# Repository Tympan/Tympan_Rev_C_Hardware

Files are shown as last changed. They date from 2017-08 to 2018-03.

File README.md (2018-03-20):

# Tympan_Rev_C_Hardware
Repository for the board files for Tympan Rev C

These design files were made with [KiCAD](http://kicad-pcb.org/) PCB capture software. The custom component files for parts used in this design are located in the repo as well. Everything should render correctly in the Schematic and the PCB. If not, you may need to adjust the library paths. 

This work is based on work done by Creare and their team in Spring of 2017. Modifications have been made to their Rev A hardware design to overcome bugs and improve the design. 

## Works with Teensy 3.6
The [Teensy 3.6](https://www.pjrc.com/store/teensy36.html) from PJRC is the 'brain' that drives our audio board. In order to make the Tympan and the Teensy live happily together, you will need to modify the Teensy board as shown.

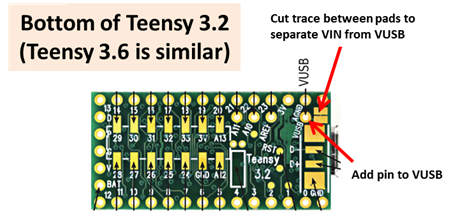
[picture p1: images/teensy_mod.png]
Teensy_Mod


The change allows us to use the VUSB (5V) to charge the LiIon battery with circuitry on the Tympan. That's it! Follow the [getting started guide](https://www.pjrc.com/teensy/first_use.html) for the Teensy, and then you will be up and running with our [Tympan Library](https://github.com/Tympan/Tympan_Library) for Arduino!

## Enclosure
The Tympan Case is 3D printed, and the design files can be found [here](https://github.com/Tympan/Tympan_Rev_C_Hardware/tree/master/Enclosure) There is also a Bill of Materials that will list the screws and threaded inserts that we used. 

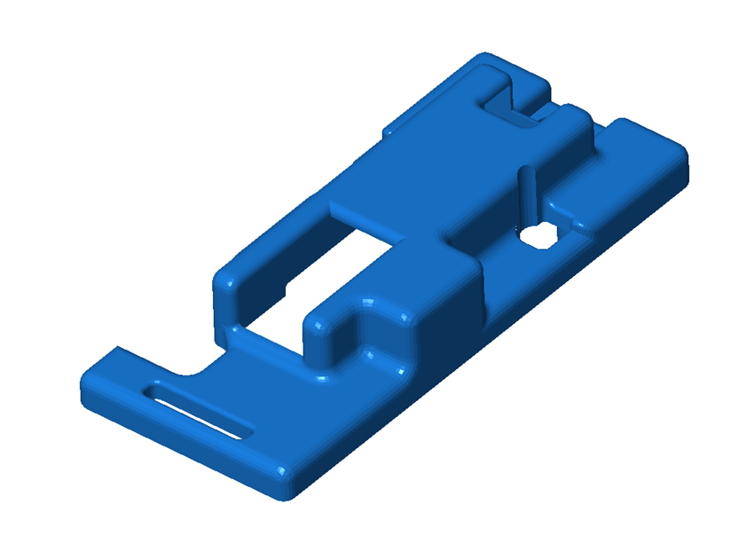
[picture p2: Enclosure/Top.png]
Tympan Case Top

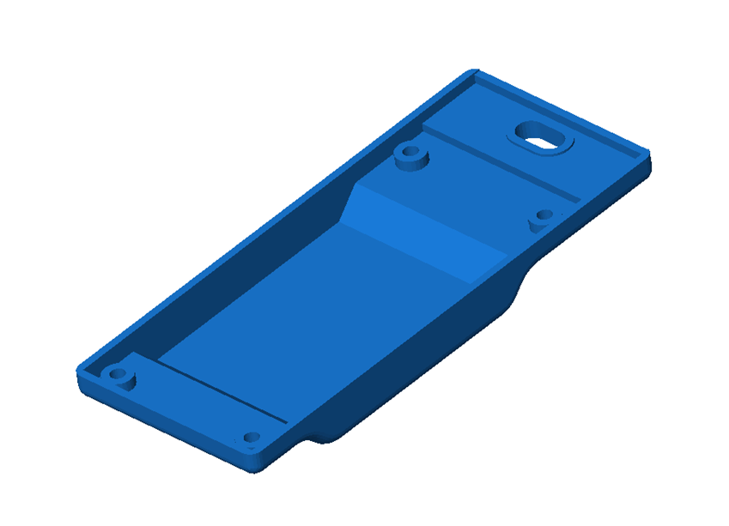
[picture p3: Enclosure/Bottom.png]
Tympan Case Bottom


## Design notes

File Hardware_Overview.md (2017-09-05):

# Tympan Hardware Overview
## Tympan Audio Board RevC

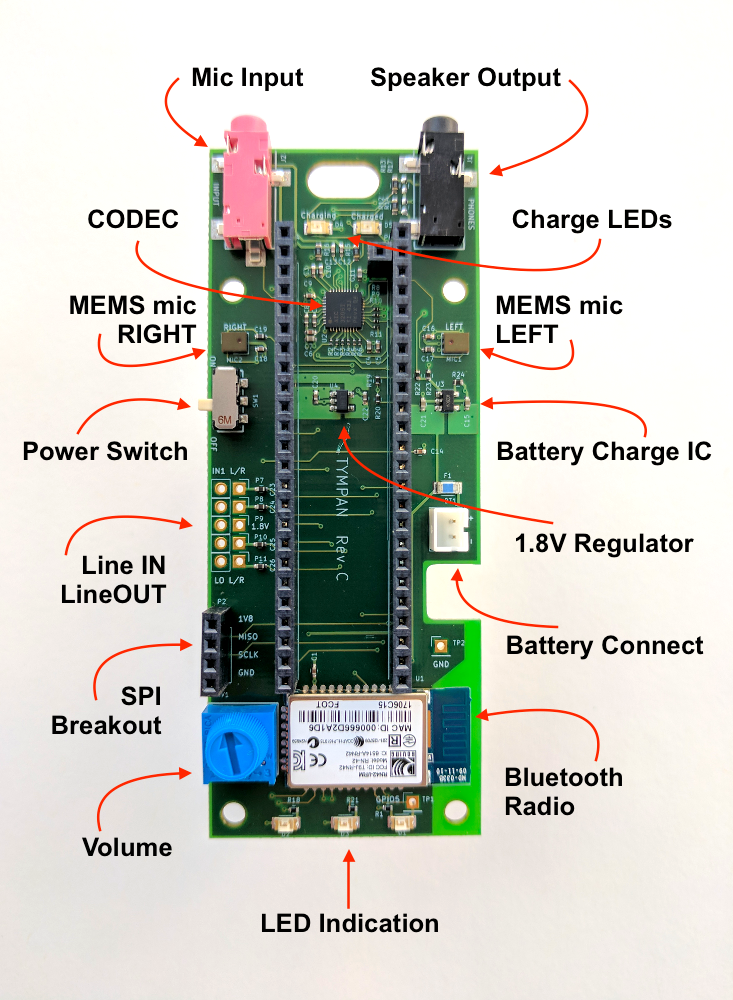
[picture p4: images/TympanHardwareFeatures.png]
Tympan Under The Hood


## Tympan assembled with Teensy 3.6

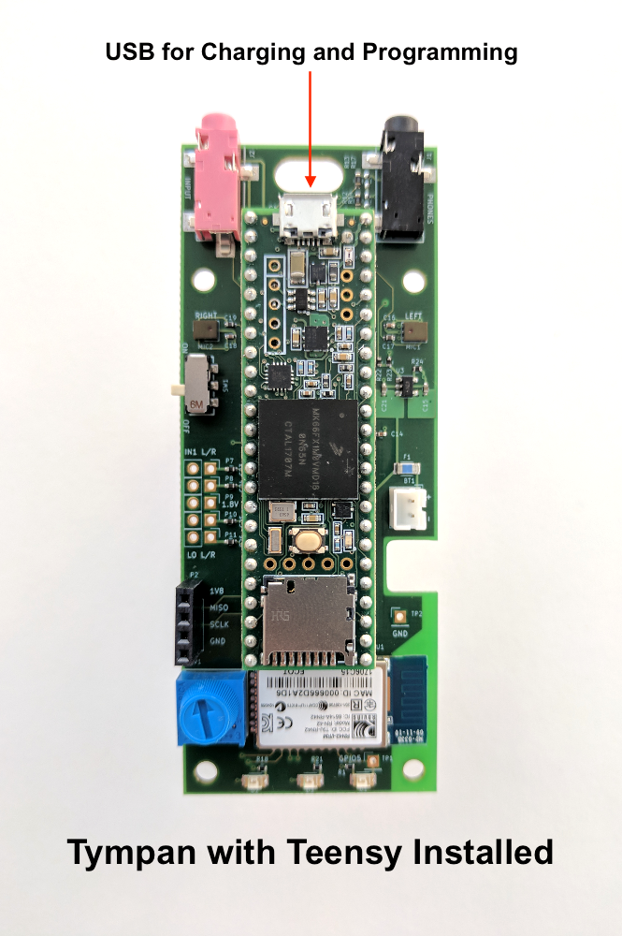
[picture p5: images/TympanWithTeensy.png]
Naked Tympan


## Hardware Modifications 

The Tympan RevC is Open Source Hardware, and that means that you can hack it or mod it and we will be here to help! There are a couple of possible mods that are baked into the hardware.

### Mic Input Jack

The MIC input jack is the pink one. The way that it has been wired to the CODEC causes the following things to happen when you plug into it:

* Mono consumer MIC (one element), you get mono into Tympan
* Stereo consumer MIC (two elements), you get mono (just the left mic is active)
* Hearing-Aid MIC (one element), you get mono into Tympan
* Stereo line-in, you get stereo into Tympan

It is possible to modify the hardware to change the MIC Input Jack behavior. If you add a 2.2K Resistor to the unpopulated R16 position, you will change the MIC input behavior to:

* Mono consumer mic (one element), you get mono into Tympan
* Stereo consumer mic (two elements), you get stereo
* Hearing-Aid Mic (one element), you get nothing
* Stereo line-in, you get nothing

### Line IN / OUT

We have broken out the `IN1` RIGHT and LEFT channels for your use. Also, the CODEC has a Line OUT channel which is also broken out. The pins available are laid out in standard 0.1" pitch, and can be soldered to as you see fit. We also breakout the 1.8V power line between them for your use a a bias voltage. You're welcome ;)

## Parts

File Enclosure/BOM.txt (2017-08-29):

Bill of Materials:

1	Tympan Rev C
1	Teensy 3.6 with 0.1" header pins soldered to each row
		- Modify Teensy by cutting trace to seperate VIN from VUSB
		- Modify Teensy by adding single 0.1" pin to VUSB through hole
1	Enclosure Top (10000200_r2)
1	Enclosure Bottom (10000167 rev3)
4	Stainless Screw-to-Expand Inserts for Plastics (McMaster-Carr P/N: 92394A112)
4	5/16" Stainless Phillips Rounded Head Screws (McMaster-Carr P/N: 91772A107)
1	Lithium Ion Polymer Battery, 3.7v 500mAh (Adafruit: Product ID 1578)

Also, add Kapton tape to bottom of Tympan PCB to electrically isolate it from the battery.

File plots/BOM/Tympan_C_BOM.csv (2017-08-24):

Id | Designator | Package | Quantity | Designation | Manufacturer | Part Number
1 | BT1 | JST_PH_B2B-PH-K_02x2.00mm_Straight | 1 | LiPo | JST Sales | B2B-PH-K-S(LF)(SN)
2 | D2,D4 | C_1206 | 2 | LED, Red | Lite-On | LTST-C150EKT
3 | D1 | C_1206 | 1 | LED, Blue | Lite-On | LTST-C150TBKT
4 | D3 | C_1206 | 1 | LED, Amber | Lite-On | LTST-C150AKT
5 | D5 | C_1206 | 1 | LED, Green | Lite-On | LTST-C150GKT
6 | F1 | C_1206 | 1 | FUSE | Bell Fuse | C1Q 1
7 | MIC2,MIC1 | SPH1642HT5H | 2 | SPH1642HT5H-1 | Knowles | SPH1642HT5H-1
8 | TP1,TP2 | DNP | 2 | DNP | DNP | DNP
9 | P5 | Pin_Header_Straight_1x01_Pitch2.54mm | 3 | CONN_01X01 | Samtec | SSW-101-01-G-S
10 | P2 | Pin_Header_Straight_1x04_Pitch2.54mm | 1 | CONN_01X04 | Samtec | SSW-104-01-G-S
11 | P4,P6 | Pin_Header_Straight_1x24_Pitch2.54mm | 2 | CONN_01X24 | Samtec | SSW-124-01-G-S
12 | P7,P8,P9,P10,P11 | DNP | 5 | DNP | DNP | DNP
13 | R12,R13 | C_0603 | 2 | 0R | Vishay Dale | CRCW06030000Z0EA
14 | R14,R16,R17 | DNP | 3 | DNP | DNP | DNP
15 | RV1 | Bourns_3386F | 1 | POT | Bourns | 3386F-1-103TLF
16 | SW1 | CL-SB-22A | 1 | CL-SB-22A | Copal | CL-SB-22A-11T
17 | U1 | RN42 | 1 | RN42 | Microchip | RN42-I/RM
18 | U2 | UQFN-40-1EP_5x5mm_Pitch0.4mm | 1 | TLV320AIC3206IRSBT | Texas Insturment | TLV320AIC3206IRSBT
19 | U3 | SOT-23-5 | 1 | MCP73831 | Microchip | MCP73831T-2ACI/OT
20 | U4 | SOT-23-5 | 1 | LP5907MFX-1.8 | Texas Insturment | LP5907MFX-1.8/NOPB
21 | J2 | SJ-3524-SMT-TR | 1 | SJ-3524-SMT-TR-PI | CUI Inc | SJ-3524-SMT-TR-PI
22 | J1 | SJ-3523-SMT-TR | 1 | SJ-3523-SMT-TR | CUI Inc | SJ-3523-SMT-TR
23 | C1,C3,C5,C7,C10,C12,C13,C14,C16,C18 | C_0402 | 10 | 0.1uF | TDK Corporation | C1005X7R1H104K050BB
24 | C2,C8,C17,C19,C23,C24,C25,C26 | C_0402 | 8 | 2.2uF | TDK Corporation | C1005X6S1C225K050BC
25 | C4,C6,C11,C15,C21 | C_0402 | 5 | 10uF | Samsung | CL05A106MP5NUNC
26 | C9,C20,C22 | C_0402 | 3 | 1uF | TDK Corporation | C1005X5R1C105K050BC
27 | R1,R18,R21,R22,R23 | R_0402 | 5 | 220R | Vishay Dale | CRCW0402220RFKED
28 | R19,R20 | R_0402 | 2 | 1K | Vishay Dale | CRCW04021K00FKED
29 | R24 | R_0402 | 1 | 2K | Vishay Dale | CRCW04022K00FKED
30 | R2,R3,R4,R5,R6,R7,R8,R9,R10,R11 | R_0201_NoSilk | 10 | 33R | Yageo | RC0201FR-0733RL
31 | R15 | C_0603 | 1 | 2.2K | Vishay Dale | CRCW06032K20FKEAHP

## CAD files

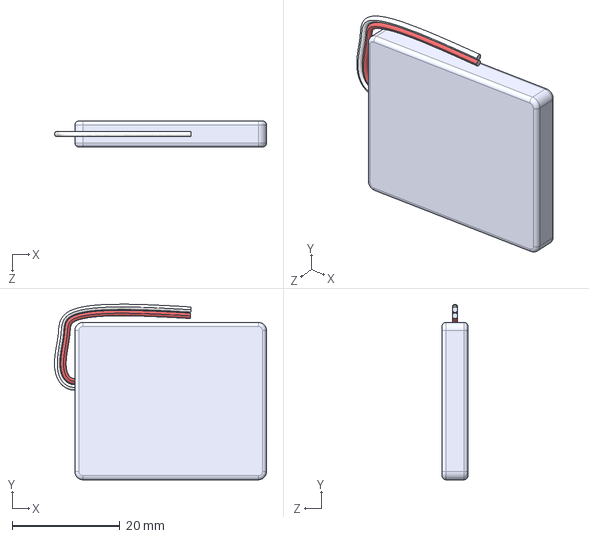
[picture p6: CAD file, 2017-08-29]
Enclosure/SolidModelOfPCB/Lithium Ion Battery.step
39.3 x 32.6 x 4.83 mm

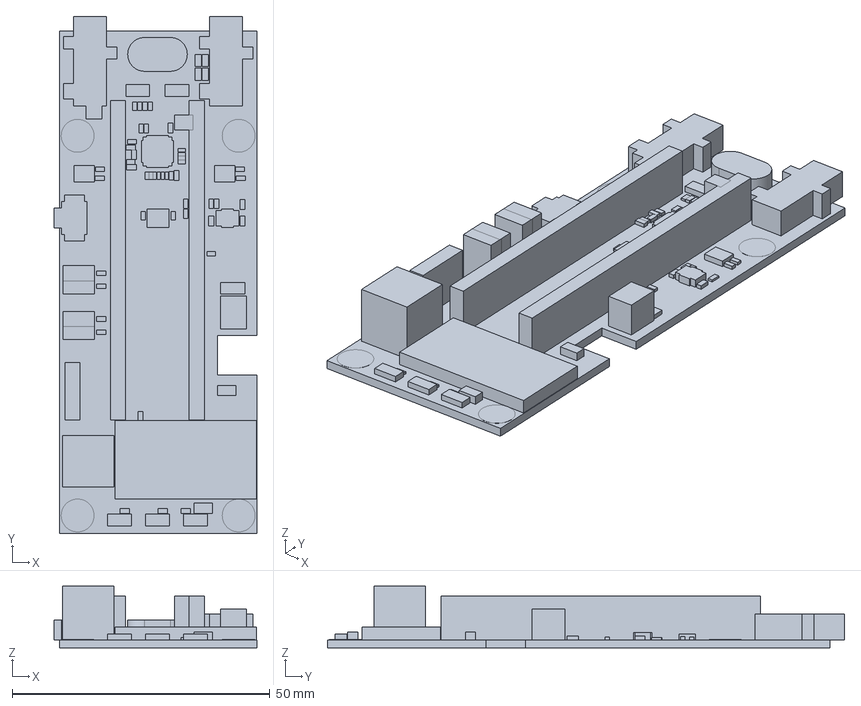
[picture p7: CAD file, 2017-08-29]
Enclosure/SolidModelOfPCB/7146-0012_PCB_Rev-A.STP
39.4 x 100.3 x 12.0 mm
BOARD_OUTLINE
COPAL_CL-SB-22A-1
RESC1609X50N x 4
SAMTEC_SSW-124-XX-X-S x 2
SAMTEC_SSW-104-XX-X-S
SAMTEC_SSW-101-XX-X-S
SLOT1000X500MECH
FUSC3216X78N
MTG_4 x 4
MICROCHIP_RN42
TP340X180N x 2
PH_B2B-PH-K-S
RESC0603X26N x 10
RESC100X50X40L25 x 2
RESC1005X40N x 8
SAMTEC_SSW-102-XX-X-S x 4
CAPC1005X55N x 13
LEDC3216X110N x 5
CAPC1005X70N x 5
CAPC1005X65N x 8
BOURNS_3386F-KNOB
CUI_SJ-3523-SMT
CUI_SJ-3524-SMT
SOT23-5P95_270X145L35X35
SOT95P280X145-5N
KNOWLES_SPH1642HT5H-1 x 2
QFN40P500X500X80-41N

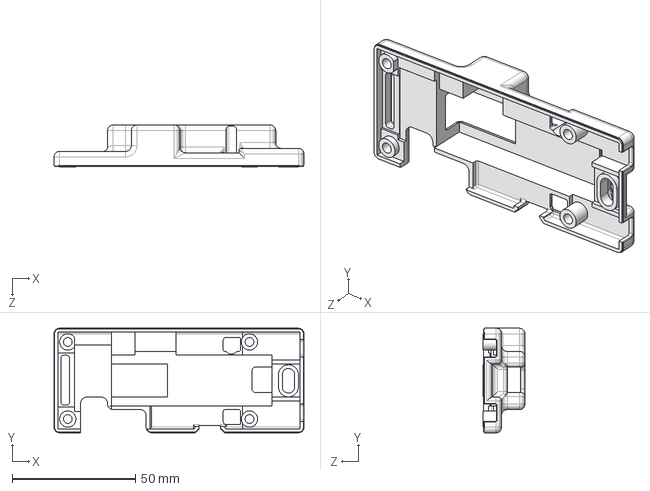
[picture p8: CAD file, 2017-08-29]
Enclosure/STEP/10000200_r2.step
101.3 x 42.4 x 17.0 mm

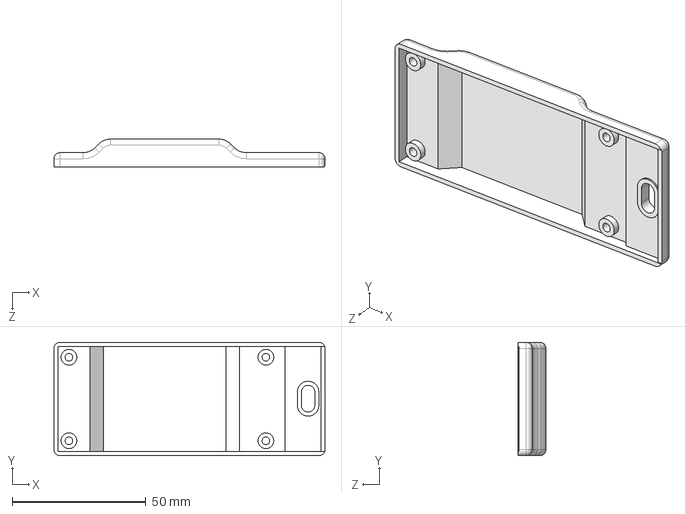
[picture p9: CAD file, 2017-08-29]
Enclosure/STEP/10000167 rev3.step
101.3 x 42.4 x 10.4 mm

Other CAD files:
Enclosure/SolidModelOfPCB/Lion Ion Battery.stl
Enclosure/STL/10000167 rev3.stl
Enclosure/STL/10000200_r2.stl

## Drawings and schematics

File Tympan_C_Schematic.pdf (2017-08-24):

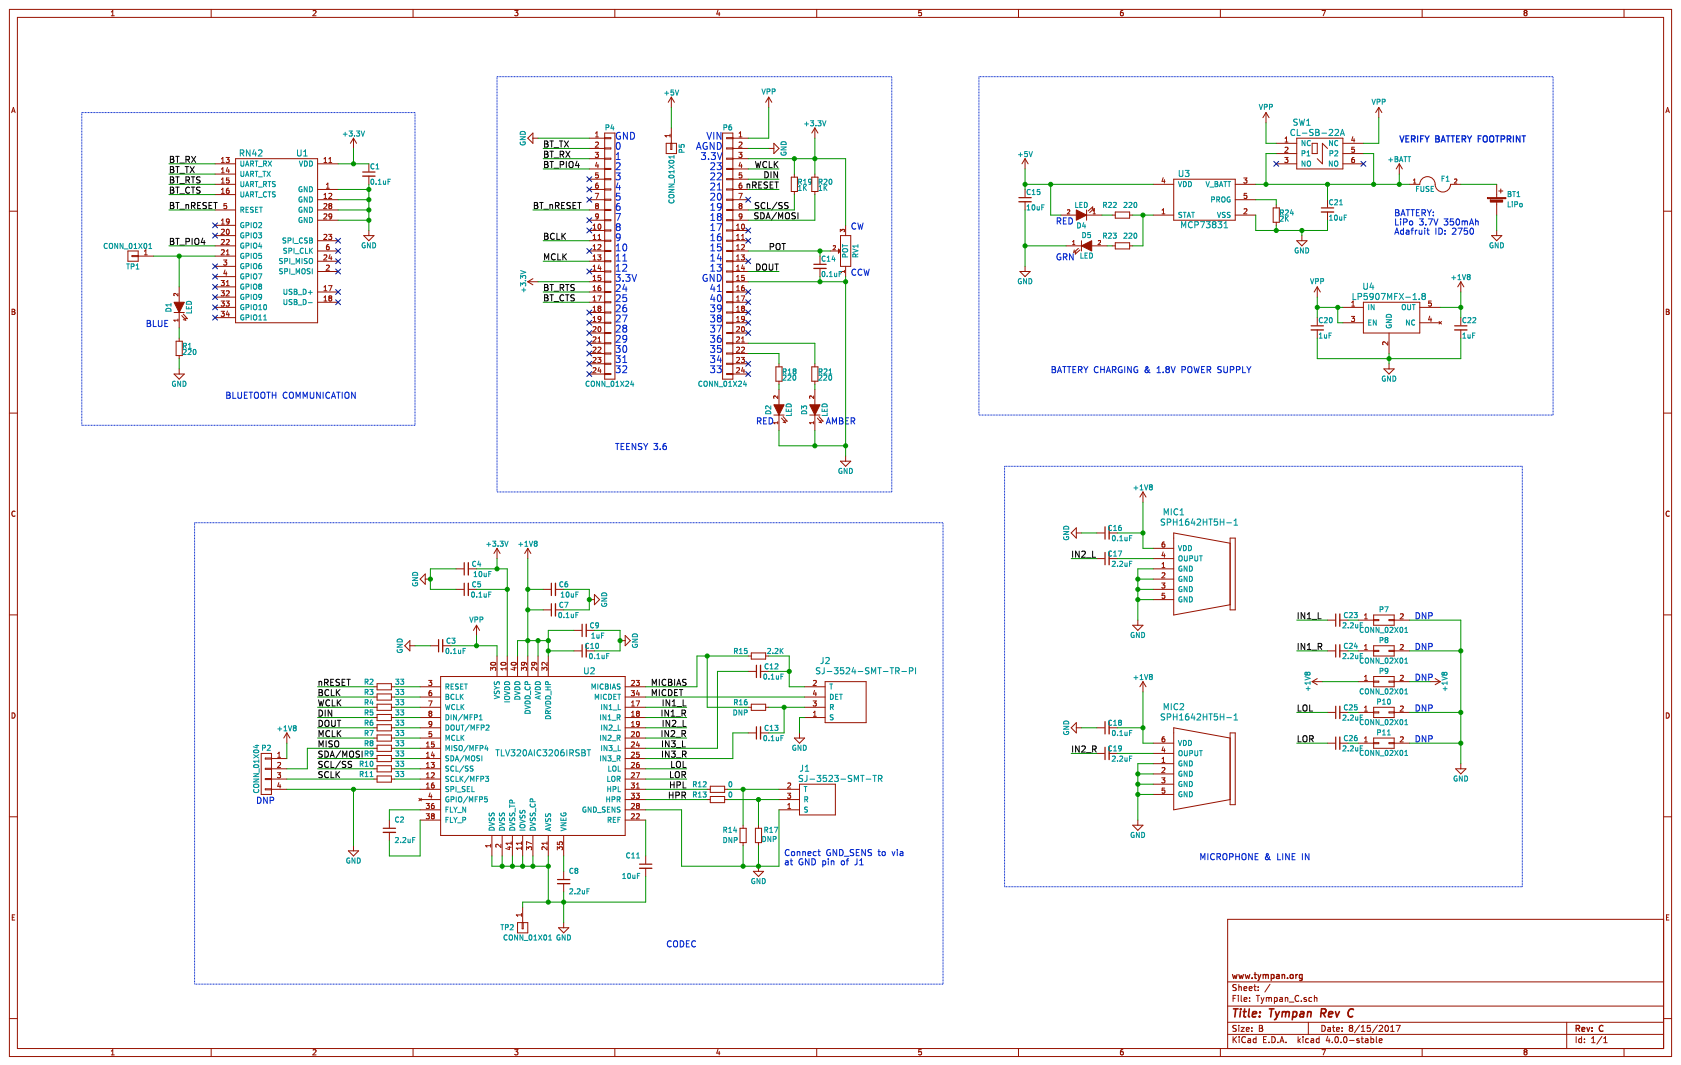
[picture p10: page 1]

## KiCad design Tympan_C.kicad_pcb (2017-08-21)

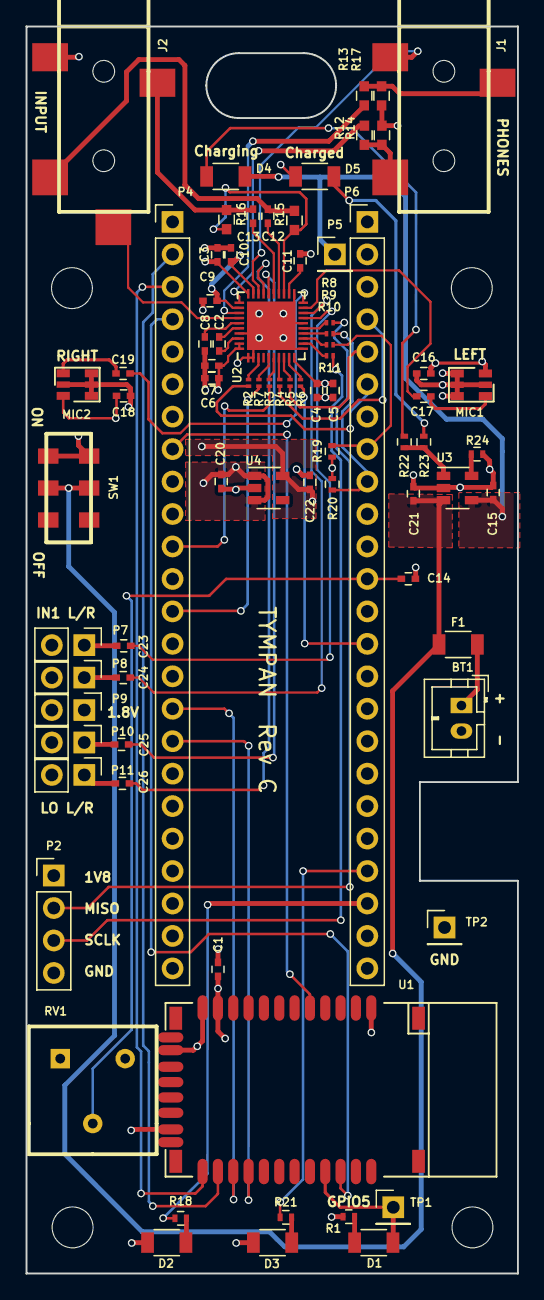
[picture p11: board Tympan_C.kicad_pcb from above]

Board: 4 copper layers, 38.5 x 97.6 mm, 78 parts (0 on the bottom side), 70 nets.

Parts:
BT1: LiPo; JST_PH_B2B-PH-K_02x2.00mm_Straight
C1, C3, C5, C7, C10, C12, C13, C14, C16, C18: 0.1uF; C_0402
C2, C8, C17, C19, C23, C24, C25, C26: 2.2uF; C_0402
C4, C6, C11, C15, C21: 10uF; C_0402
C9, C20, C22: 1uF; C_0402
D1, D2, D3, D4, D5: LED; C_1206
F1: FUSE; C_1206
J1: SJ-3523-SMT-TR
J2: SJ-3524-SMT-TR-PI; SJ-3524-SMT-TR
MIC1, MIC2: SPH1642HT5H-1; SPH1642HT5H
P2: CONN_01X04; Pin_Header_Straight_1x04_Pitch2.54mm
P4, P6: CONN_01X24; Pin_Header_Straight_1x24_Pitch2.54mm
P5: CONN_01X01; Pin_Header_Straight_1x01_Pitch2.54mm
P7, P8, P9, P10, P11: CONN_02X01; Pin_Header_Straight_1x02_Pitch2.54mm
R1, R18, R21, R22, R23: 220; R_0402
R2, R3, R4, R5, R6, R7, R8, R9, R10, R11: 33; R_0201_NoSilk
R12, R13, R15, R16: 0; C_0603
R14, R17: DNP; C_0603
R19, R20: 1K; R_0402
R24: 2K; R_0402
RV1: POT; Bourns_3386F
SW1: CL-SB-22A
TP1, TP2: CONN_01X01; Pin_Header_Straight_1x01_Pitch2.54mm
U1: RN42
U2: TLV320AIC3206IRSBT; UQFN-40-1EP_5x5mm_Pitch0.4mm
U3: MCP73831; SOT-23-5
U4: LP5907MFX-1.8; SOT-23-5

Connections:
+1V8: C6.1, C7.1, C9.1, C10.1, C16.2, C18.2, C22.1, MIC1.6, MIC2.6, P2.1, P9.1, P9.2, U2.29, U2.32, U2.39, U2.40, U4.5
+3V3: C1.1, C4.2, C5.2, P4.15, P6.3, R19.1, R20.1, RV1.3, U1.11, U2.10
+5V: C15.1, D4.2, P5.1, U3.4
+BATT: C21.1, F1.1, SW1.2, SW1.5, U3.3
/BCLK: P4.11, R3.1
/BT_CTS: P4.17, U1.16
/BT_PIO4: P4.4, U1.22
/BT_RTS: P4.16, U1.15
/BT_RX: P4.3, U1.13
/BT_TX: P4.2, U1.14
/BT_nRESET: P4.8, U1.5
/DIN: P6.5, R5.1
/DOUT: P6.14, R6.1
/HPL: R12.1, U2.31
/HPR: R13.1, U2.33
/IN1_L: C23.1, U2.17
/IN1_R: C24.1, U2.18
/IN2_L: C17.1, U2.19
/IN2_R: C19.1, U2.20
/IN3_L: C12.1, U2.24
/IN3_R: C13.1, U2.25
/LOL: C25.1, U2.26
/LOR: C26.1, U2.27
/MCLK: P4.13, R7.1
/MICBIAS: R15.1, R16.1, U2.23
/MICDET: J2.4, U2.34
/MISO: P2.2, R8.1
/POT: C14.1, P6.12, RV1.2
/SCL/SS: P6.8, R10.1, R19.2
/SCLK: P2.3, R11.1
/SDA/MOSI: P6.9, R9.1, R20.2
/WCLK: P6.4, R4.1
/nRESET: P6.6, R2.1
GND: BT1.2, C1.2, C3.1, C4.1, C5.1, C6.2, C7.2, C8.2, C9.2, C10.2, C11.2, C14.2, C15.2, C16.1, C18.1, C20.2, C21.2, C22.2, D2.1, D3.1, D5.1, J1.1, J2.1, MIC1.1, MIC1.2, MIC1.3, MIC1.5, MIC2.1, MIC2.2, MIC2.3, MIC2.5, P2.4, P4.1, P6.2, P6.15, P7.2, P8.2, P10.2, P11.2, R1.2, R14.2, R17.2, R24.2, RV1.1, TP2.1, U1.1, U1.12, U1.28, U1.29, U2.1, U2.2, U2.11, U2.16, U2.21, U2.28, U2.37, U2.41, U3.2, U4.2
unnamed: BT1.1, F1.2
unnamed: C2.1, U2.36
unnamed: C2.2, U2.38
unnamed: C8.1, U2.35
unnamed: C11.1, U2.22
unnamed: C12.2, J2.2, R15.2
unnamed: C13.2, J2.3, R16.2
unnamed: C17.2, MIC1.4
unnamed: C19.2, MIC2.4
unnamed: C23.2, P7.1
unnamed: C24.2, P8.1
unnamed: C25.2, P10.1
unnamed: C26.2, P11.1
unnamed: D1.1, R1.1
unnamed: D1.2, TP1.1, U1.21
unnamed: D2.2, R18.2
unnamed: D3.2, R21.2
unnamed: D4.1, R22.1
unnamed: D5.2, R23.1
unnamed: J1.2, R12.2, R14.1
unnamed: J1.3, R13.2, R17.1
unnamed: P6.21, R21.1
unnamed: P6.22, R18.1
unnamed: R2.2, U2.3
unnamed: R3.2, U2.6
unnamed: R4.2, U2.7
unnamed: R5.2, U2.8
unnamed: R6.2, U2.9
unnamed: R7.2, U2.5
unnamed: R8.2, U2.15
unnamed: R9.2, U2.14
unnamed: R10.2, U2.13
unnamed: R11.2, U2.12
unnamed: R22.2, R23.2, U3.1
unnamed: R24.1, U3.5
VPP: C3.2, C20.1, P6.1, SW1.1, SW1.4, U2.30, U4.1, U4.3

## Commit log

2017-08-21 Committing Design and Production files
    [Tympan_C-B.Cu.gbr, Tympan_C-B.Mask.gbr, Tympan_C-B.Paste.gbr, Tympan_C-B.SilkS.gbr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]
2017-08-24 Updated BOM
    Updated BOM to specify R16 as DNP and R15 as 2K2R
    [Tympan_C_BOM.csv]
2017-08-24 Updated schematic
    changed R15 to 2.2K
    changed R16 to DNP
    [Tympan_C.sch]
2017-08-29 Added print files and teensy mod
    Added info on how to mod the Teensy 3.6 and also 3D print files for the
    enclosure
    [10000167 rev3.step, 10000167 rev3.stl, 10000200_r2.step, 10000200_r2.stl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]
